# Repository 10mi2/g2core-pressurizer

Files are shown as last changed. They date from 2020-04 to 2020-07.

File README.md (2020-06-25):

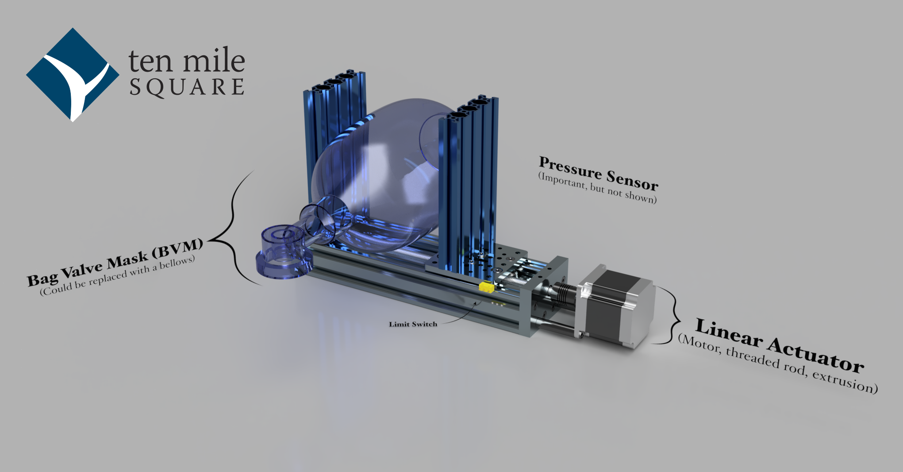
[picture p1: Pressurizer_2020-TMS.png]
Pressurizer simplified image


# g2core Pressurizer

A prototype emergency ventilator project based on [g2core](https://github.com/synthetos/g2/tree/pressurizer)

# Flow sensor

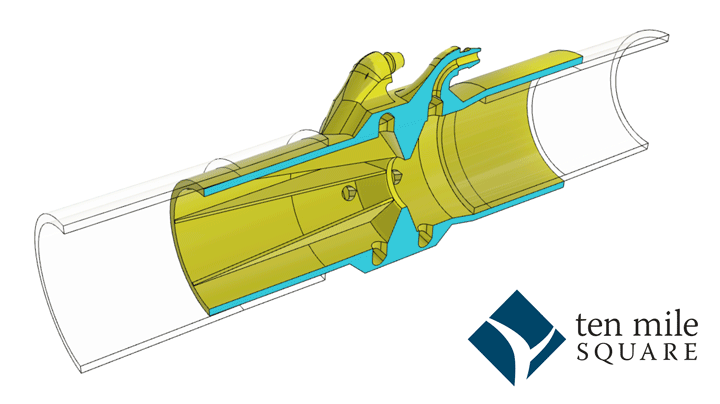
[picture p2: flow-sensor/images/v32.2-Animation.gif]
Flow sensor animation


As a subproject, a 3D-printable and home-manufacturable flow sensor that can be used for any ventilator or stand-alone can be found in the [flow-sensor](flow-sensor) subdirectory.

# What is this?

See the blog posts [Designing an Intelligent IoT Ventilator From Home, Pt. 1](https://tenmilesquare.com/designing-an-intelligent-iot-ventilator-from-home-pt-1/) for an introduction and [Designing an Intelligent IoT Ventilator From Home, Pt. 2](https://tenmilesquare.com/designing-an-intelligent-iot-ventilator-from-home-pt-2/) for more detailed theory of operation.

# State of the project

- [x] Build proof-of-concept (POC) firmaware and hardware solution and verify minimal functionality [video here](https://youtu.be/bmQI65D5-_8)
- [X] Document theory of operation located in the **second blog post here**
- [X] [Document Bill-of-materials (BOM) for POC with links for ordering](Bill-of-Materials.md)
- [ ] Document firmware build process
- [ ] Document hardware build process
- [ ] Build and test physical UI firmware
- [ ] Build remote IoT control capability
  - [ ] GrapQL / MQTT Service
  - [ ] Web UI

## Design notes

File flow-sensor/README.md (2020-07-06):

Flow sensor animation

# g2Core Pressurizer Flow Sensor

This project [described in this blog post](https://tenmilesquare.com/designing-and-building-a-ventilator-flow-sensor-from-home-pt-3/) provides a flow sensor that may be used completely independently of the Pressurizer.

# Downloads

| Version | Links |
| ---- | --- |
| v32.2 | [STL](./flow-sensor-v32.2.stl) - [Fusion360](https://a360.co/2NsMhkD) |
| v32.2 - flow ports only | [STL](./flow-sensor-v32.2-no-pressure-port.stl) - [Fusion360](https://a360.co/2C7vkd5) |
| pressure adapter only (**not** a flow sensor) | [STL](./pressure-port-adapter.stl) - [Fusion360](https://a360.co/2Az5AWq) |

# Instructions

## Printable version

Tested by printing with PETG, but PLA should work as well. Print oriented on it's end with the ports pointing **up**. This will leave little contact with the bed, so you'll need to make sure your bed is clean and prepared properly for your type of printer and meaterial. On the Prusa MK3s, that means cleaned with dish soap thoroughly (every 4-5 prints) and then a thin layer of glue stick applied where the print will land and the bottom left corner where it primes the extruder.

### Print Settings:
- NO support (unless you have disolvable support)
- 0.15mm layer height or less (thinner layers are better)
- 15% infill (can be adjusted, not much infill on this one)
- Designed for a 0.4mm nozzle, so that most of the walls are exactly three perimeters width. The wall thickness is a parameter in Fusion360 if it needs to be adjusted

# Python Monitor Usage

The python monitor needs cleaned up and made more user-friendly, but in the interest of getting stuff out there, I'm posting it now as-is.

- Clone or download this repo to a Raspberry Pi (or any machine supported by the [Sparkfun Qwiic Python library](https://github.com/sparkfun/qwiic_py#supported-platforms))
- Make sure you have `python3` and `pip3` installed
- In a terminal (one time, for installation)
  ```bash
  cd flow-sensor/python-flow-sensor-monitor
  pip install -r requirements.txt
  ```
- For now, you have to alter the code for the flow sensors you have
- Near the end, choose what output style you'd like, comment the ones you don't, uncomment the one you do
- Call it:
  ```bash
  ./flow-sensor-monitor.py
  # or to make a csv file
  ./flow-sensor-monitor.py > test-output.csv
  ```
- When you're done, hit `Ctrl-C` (maybe twice) to make it stop

# Calibration Jupyter

The file [`flow-sensor/calibration.ipynb`](./flow-sensor/calibration.ipynb) can be opened with a [local Jupyter server](https://jupyter.org) (or [VSCode with the Python extension installed](https://code.visualstudio.com/docs/python/jupyter-support)).

Notes:
- Record a series of tests with the same filename except for a number. For example `cal-v32.2-2020-06-29-001.csv`, `cal-v32.2-2020-06-29-002.csv`, etc.
- Set `start_k` is the K value used in `flow-sensor-monitor.py` when recording the tests.
- Run the full notebook, and along with some nice charts showing your data, you'll find a new K value to use in the last (bottom) cell.
- Note that it'll clip the first part of each file until the flow reaches > +-10slm, and then keep only 4 seconds from there.

# On the way

- List of sensors that are usable
- Assembly instructions
- More complete calibration instructions, building on those in the [blog post](https://tenmilesquare.com/designing-and-building-a-ventilator-flow-sensor-from-home-pt-3)

# TODO

- Cleanup the python to take a configuration file and command line options.
- Provide calibration Excel / google sheets templates

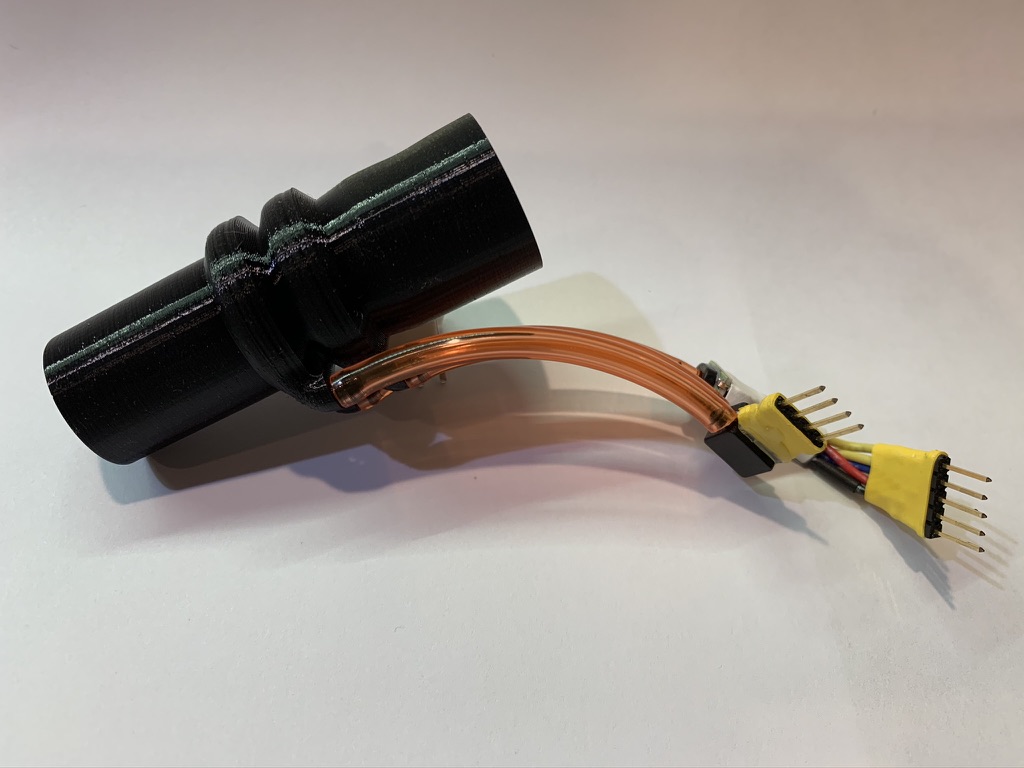
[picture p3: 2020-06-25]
flow-sensor/images/v31-all-connected.jpeg

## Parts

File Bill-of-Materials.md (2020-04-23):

# Ten Mile Square g2core Pressurizer Bill-of-Materials

This is the parts list we used to build our proof of concept, and unless otherwise noted the parts can be replaced by similar. Please note that we are listing what worked for us, and should be sufficient to get you started.

## Mechanical

- [OpenBuilds C-Beam® Linear Actuator Bundle](https://openbuildspartstore.com/c-beam-linear-actuator-bundle/) - 250mm version
  - [Add the High-Torque NEMA-23 Motor](https://openbuildspartstore.com/nema-23-stepper-motor-high-torque-series/) - the normal NEMA-23 _might_ work but our testing shows that we're near the torque limit of this motor
- [OpenBuilds V-Slot® 20x80 Linear Rail](https://openbuildspartstore.com/v-slot-20x80-linear-rail/) - at _least_ 250mm length, this will be cut into two lengths
- Corner brackets - at _least_ 6 - [Angle Corner Connector](https://openbuildspartstore.com/black-angle-corner-connector/) (Needs tested: may be able to only use 4 total for cost reduction)
  - To save money, *at most two of them* may be able to be replaced with these [cast version](https://openbuildspartstore.com/cast-corner-bracket/) *or* [these hidden ones](https://openbuildspartstore.com/inside-hidden-corner-bracket/)
- 1 x [Tee Nuts - M5 (10 Pack)](https://openbuildspartstore.com/tee-nuts-m5-10-pack/) - only two are needed, but they're sold in 10-packs
- 1 x *8mm* [Low Profile Screws M5 (10 Pack)
](https://openbuildspartstore.com/low-profile-screws-m5-10-pack/) - only 4 are needed, but they're sold in 10 packs
  - You *may* use other head shaped M5 screws but the length is important - if they're too long, you may need to add washers to make it work
- 1 x *15mm* [Low Profile Screws M5 (10 Pack)
](https://openbuildspartstore.com/low-profile-screws-m5-10-pack/) (Note: Same link as the previous item, you mush choose a different size) - only 2 are needed, but they're sold in 10 packs
  - These two *must* be these low-profile kind, as they're placed so the head has to fit *under* the gantry plate without hitting the C-Beam
  - It might be possible to omit these - testing is needed
- *Optional* 2 x [Handles](https://openbuildspartstore.com/v-slot-door-handle/) - comes with the nusts and screws needed
- *Optional* Some thin (roughly 1/8" or 3mm) foam or cloth to protect the BVM from the sharp edges
- *Optional* Some tape or cloth to hold the bag in place and up from getting pinched in machinery
- 1 x Limit switch - [Option 1](https://openbuildspartstore.com/xtension-limit-switch-kit/), [Option 2](https://openbuildspartstore.com/micro-limit-switch-kit/), [Option 3](https://openbuildspartstore.com/micro-limit-switch/) - requires finding a means of attaching it
- **Tubing** - depending on what sensor you choose, you'll need to be able to place the sensor in the same pressure system as the "patient" (a test lung, in this case) - this may vary wildly

## Electrical

- Power supply - 12V or 24V power supply - *Add Links to OpenBuilds and Adafruit*
- Stepper motor driver - There are many many options. Here's the one we used: [STR3 from Applied Motion](https://www.applied-motion.com/products/STR3-miniature-advanced-microstep-drive). Here's a nice one from [OMC StepperOnline](https://www.omc-stepperonline.com/digital-stepper-driver-10-42a-20-50vdc-for-nema-17-23-24-stepper-motor-dm542t.html).
  - Notes: You'll want current capability >2A peak per channel
  - It will need to take Step/Direction and (optionally) Enable signals.
- Controller board
  - Option 1: g2core gQuintic (currently prerelease) or g2core v9k (OEM edition) - as the gQuintic is not yet released and the v9k is only sold to OEM we recommend going with option two for now
  - Option 2: Arduino Due - [Arduino Store](https://store.arduino.cc/usa/due) - [SparkFun](https://www.sparkfun.com/products/11589)
    - Most of the stepper drivers will require 5V signals, so you'll need a voltage level shifter like [this one](https://www.adafruit.com/product/757) (more convenient) or [this one](https://www.adafruit.com/product/1787) (less convenient). In either case, you'll need basic soldering skills and equipment in order to use them.
    - The Due can only handle power up to 12V before it starts to get uncomfortably hot. If you go with a 24V power supply you'll need to find some other means of safely powering the Due such as a separate power supply.
- Sensor options:
  - Tested with the Honeywell TrusAbility SSC part [SSCMRND015PGSA3](https://www.digikey.com/product-detail/en/honeywell-sensing-and-productivity-solutions/SSCMRND015PGSA3/480-5405-ND/2863940)
  - Also possible: [Bosch BPM280](https://www.digikey.com/en/datasheets/bosch-sensortec/bosch-sensortec-bst-bmp280-ds001-19) ([here on an Adafruit carrier board](https://www.digikey.com/product-detail/en/adafruit-industries-llc/2651/1528-1358-ND/5604371))

## Testing

- **Test Lungs**

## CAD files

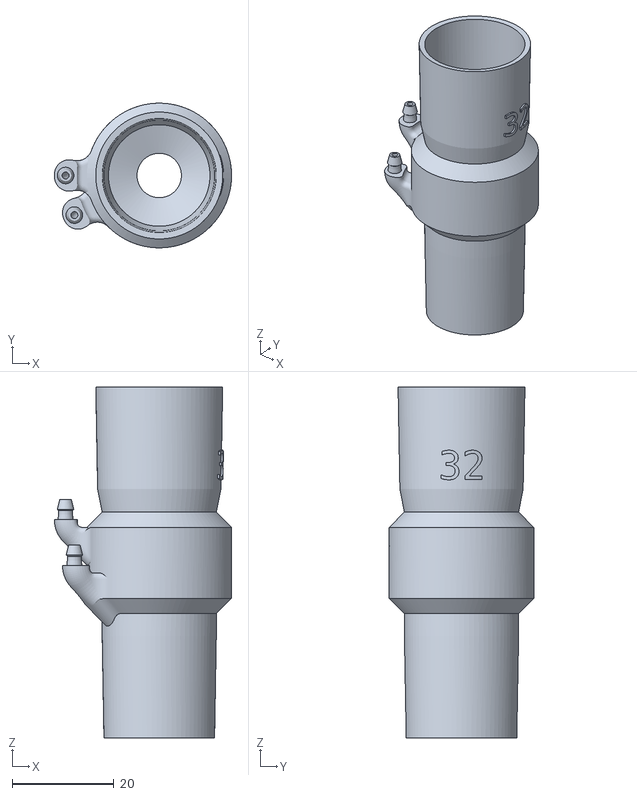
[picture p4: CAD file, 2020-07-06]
flow-sensor/flow-sensor-v32.2-no-pressure-port.stl
34.9 x 28.5 x 69.1

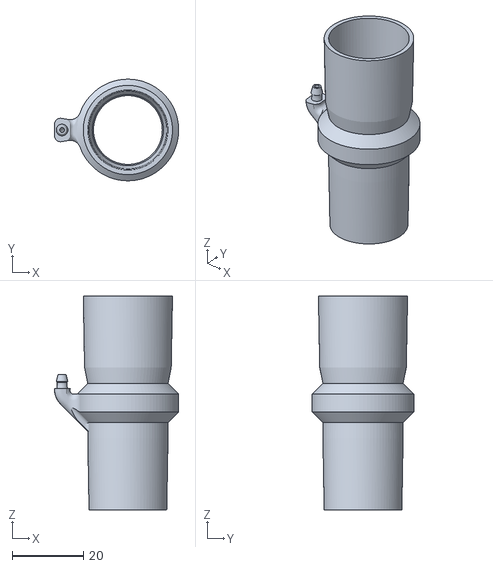
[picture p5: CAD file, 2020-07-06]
flow-sensor/pressure-port-adapter.stl
34.9 x 28.5 x 60.0

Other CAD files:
flow-sensor/flow-sensor-v32.2.stl

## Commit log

2020-06-25 Added start of flow-sensor subproject
    [flow-sensor-v32.2.stl]
2020-06-25 Made the image to the flow sensor a link
2020-06-25 Added Fusion360 link for flow sensor
2020-06-25 Adding python flow-sensor-monitor and instructions
2020-06-25 Updated flow sensor readme
2020-06-27 Add gitignore and Jupyter notebook for calibration
2020-07-01 calibration.ipynb is coming along, bu not very generally usable yet,
2020-07-06 Updated calibration Jupyter
2020-07-06 Added pressure-port free and pressure-port adapter STLs
    [flow-sensor-v32.2-no-pressure-port.stl, pressure-port-adapter.stl]
2020-07-06 Breaking flow sensor code into modules
2020-07-06 Added calibration-zero and updating calibration
2020-07-06 Fixing error in the flow-sensor-monitor and libraries
2020-07-07 Adjust calibration Jupyter to use median computed K
